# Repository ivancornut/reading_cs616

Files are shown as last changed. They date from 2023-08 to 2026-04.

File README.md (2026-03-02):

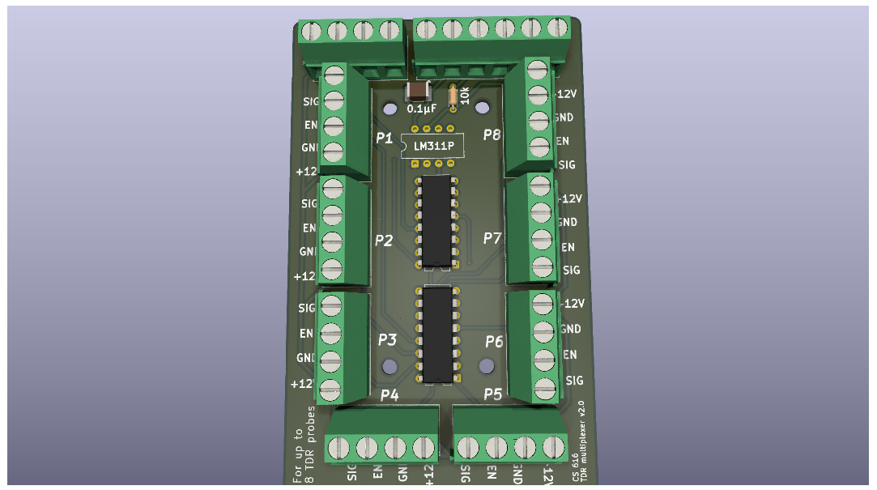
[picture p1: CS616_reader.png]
Multiplexer

# Reading CS616

The CS616 is a moisture sensor from Campbell. It measures the soil moisture using the TDR (Time domain relfectometry) technique. 
This is an efficient and accurate way to measure soil moisture. These sensors output a square wave with a period proportional to the soil moisture.
The output period is above 10 µS so readable by a Pi Pico. Unfortunately the output is a square wave from -0.7V to 0.7V which is not readable by the input pin of a 3.3V arduino micro-controller. 

The goal is to provide a way to read multiple CS616 sensors using a Pi Pico board. 

## Simple Schematic to read one sensor using a micro-controller
To convert the output of the sensor into something readable by a 3.3V µC we use a fast differential comparator, the LM311P. This idea was inspired by the design of a frequency counter found online [here](https://www.ee-diary.com/2022/07/high-frequency-counter-with-arduino.html#). Their design was adapted using an example circuit found in the datasheet of the comparator. 

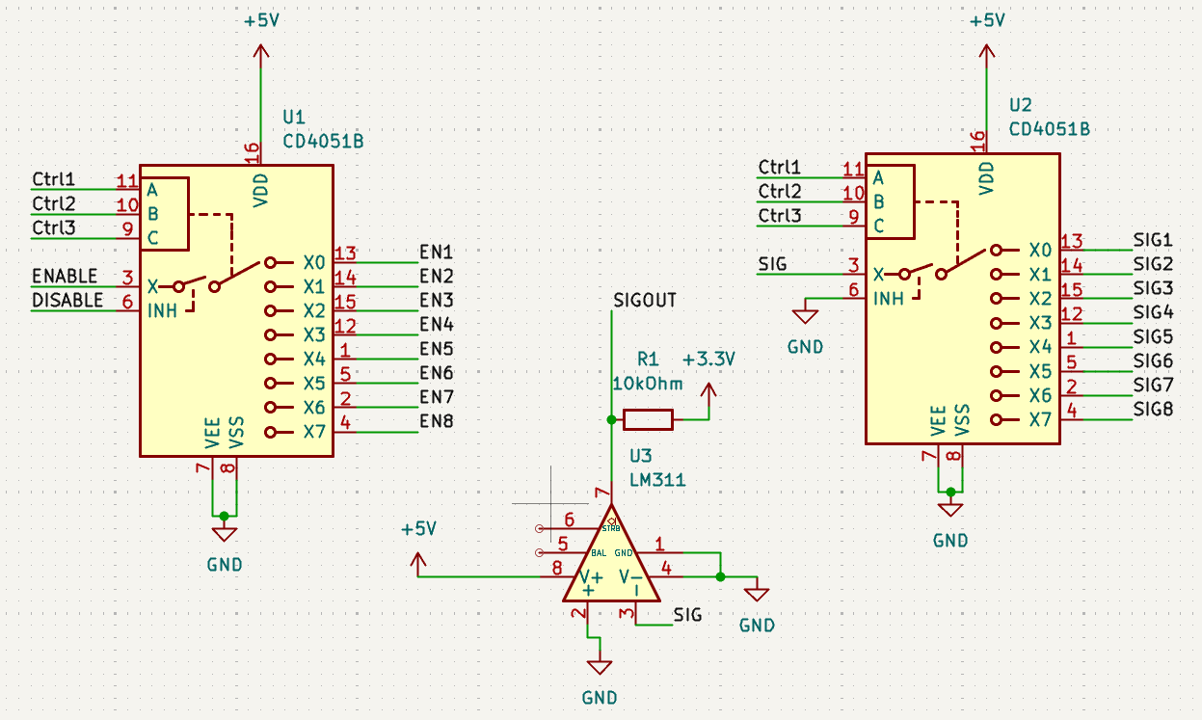
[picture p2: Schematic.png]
Comparator circuit


## Reading multiple CS616 sensors using one micro-controller
We combine the use of the comparator with the use of multiplexers that multiplex the enable and signal lines of the sensors.

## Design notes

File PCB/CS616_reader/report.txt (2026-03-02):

Info: Fini.
Info: Fini.
Tracé en '/home/cornut/Documents/dev_capteurs/reading_cs616/PCB/CS616_reader/Gerber_files/CS616_reader-F_Paste.gbr'.
Tracé en '/home/cornut/Documents/dev_capteurs/reading_cs616/PCB/CS616_reader/Gerber_files/CS616_reader-F_Paste.gbr'.
Tracé en '/home/cornut/Documents/dev_capteurs/reading_cs616/PCB/CS616_reader/Gerber_files/CS616_reader-B_Paste.gbr'.
Tracé en '/home/cornut/Documents/dev_capteurs/reading_cs616/PCB/CS616_reader/Gerber_files/CS616_reader-F_Silkscreen.gbr'.
Tracé en '/home/cornut/Documents/dev_capteurs/reading_cs616/PCB/CS616_reader/Gerber_files/CS616_reader-B_Silkscreen.gbr'.
Tracé en '/home/cornut/Documents/dev_capteurs/reading_cs616/PCB/CS616_reader/Gerber_files/CS616_reader-F_Mask.gbr'.
Tracé en '/home/cornut/Documents/dev_capteurs/reading_cs616/PCB/CS616_reader/Gerber_files/CS616_reader-B_Mask.gbr'.
Tracé en '/home/cornut/Documents/dev_capteurs/reading_cs616/PCB/CS616_reader/Gerber_files/CS616_reader-Edge_Cuts.gbr'.
Création du fichier Gerber "job" '/home/cornut/Documents/dev_capteurs/reading_cs616/PCB/CS616_reader/Gerber_files/CS616_reader-job.gbrjob'.
Tracé en '/home/cornut/Documents/dev_capteurs/reading_cs616/PCB/CS616_reader/Gerber_files/CS616_reader-B_Cu.gbr'.
Tracé en '/home/cornut/Documents/dev_capteurs/reading_cs616/PCB/CS616_reader/Gerber_files/CS616_reader-B_Cu.gbr'.
Tracé en '/home/cornut/Documents/dev_capteurs/reading_cs616/PCB/CS616_reader/Gerber_files/CS616_reader-B_Paste.gbr'.
Tracé en '/home/cornut/Documents/dev_capteurs/reading_cs616/PCB/CS616_reader/Gerber_files/CS616_reader-F_Silkscreen.gbr'.
Tracé en '/home/cornut/Documents/dev_capteurs/reading_cs616/PCB/CS616_reader/Gerber_files/CS616_reader-B_Silkscreen.gbr'.
Tracé en '/home/cornut/Documents/dev_capteurs/reading_cs616/PCB/CS616_reader/Gerber_files/CS616_reader-F_Mask.gbr'.
Tracé en '/home/cornut/Documents/dev_capteurs/reading_cs616/PCB/CS616_reader/Gerber_files/CS616_reader-B_Mask.gbr'.
Tracé en '/home/cornut/Documents/dev_capteurs/reading_cs616/PCB/CS616_reader/Gerber_files/CS616_reader-Edge_Cuts.gbr'.
Création du fichier Gerber "job" '/home/cornut/Documents/dev_capteurs/reading_cs616/PCB/CS616_reader/Gerber_files/CS616_reader-job.gbrjob'.
Tracé en '/home/cornut/Documents/dev_capteurs/reading_cs616/PCB/CS616_reader/Gerber_files/CS616_reader-F_Cu.gbr'.
Tracé en '/home/cornut/Documents/dev_capteurs/reading_cs616/PCB/CS616_reader/Gerber_files/CS616_reader-F_Cu.gbr'.
Attention: Correction de largeur. La valeur de correction doit être dans la plage  [0,000001 mm; 0,199999 mm]  pour les règles actuelles de conception.
Info: Fini.
Info: Fini.

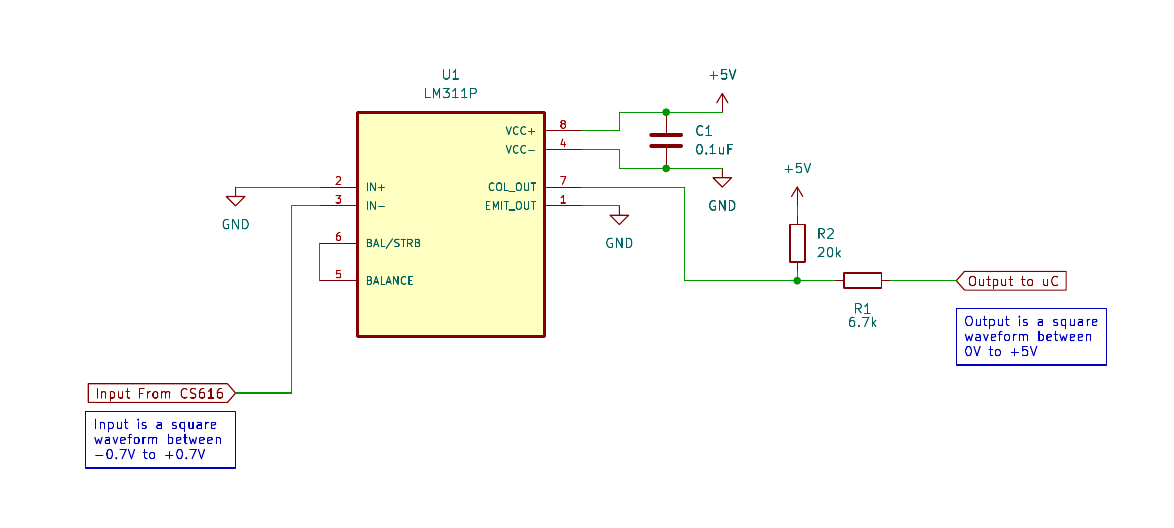
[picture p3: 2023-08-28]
Comparator_circuit.png

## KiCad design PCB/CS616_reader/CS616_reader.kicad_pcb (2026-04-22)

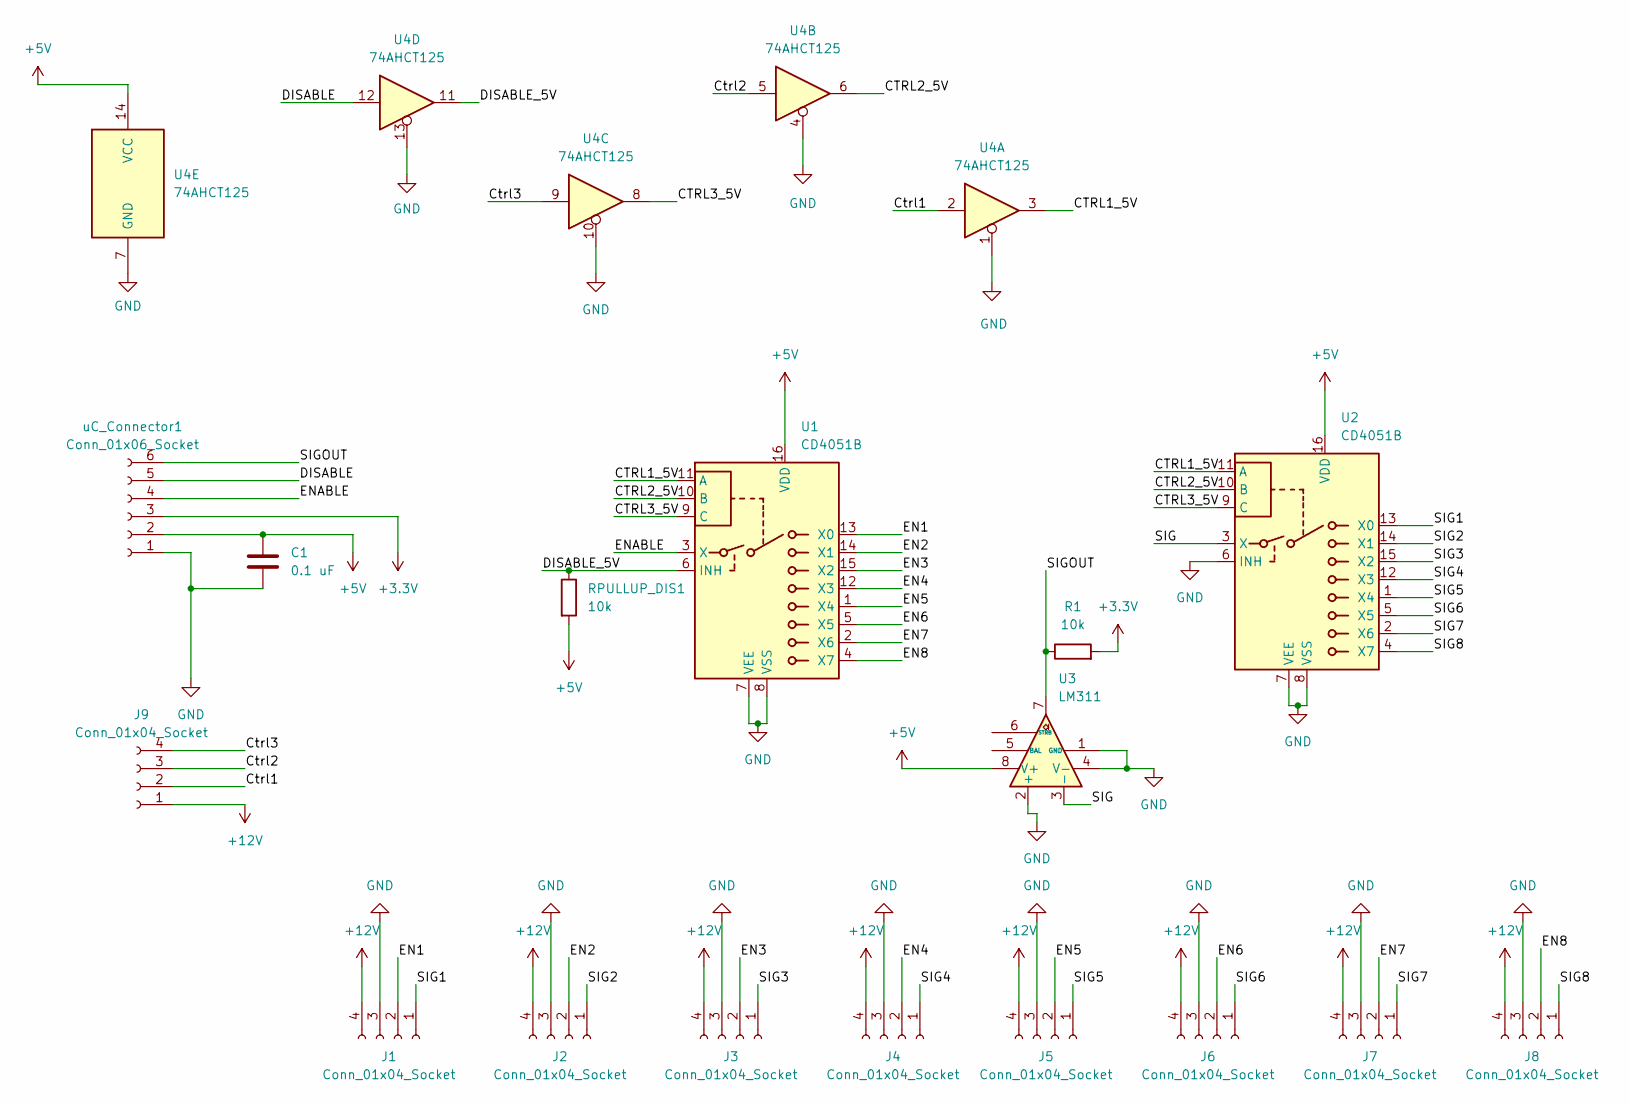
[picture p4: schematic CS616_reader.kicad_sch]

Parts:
C1: 0.1 uF; C_1812_4532Metric_Pad1.57x3.40mm_HandSolder
J1, J2, J3, J4, J5, J6, J7, J8, J9: Conn_01x04_Socket; TerminalBlock_Phoenix_MKDS-1,5-4-5.08_1x04_P5.08mm_Horizont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
R1: 10k; R_Axial_DIN0204_L3.6mm_D1.6mm_P5.08mm_Horizontal
RPULLUP_DIS1: 10k; R_Axial_DIN0204_L3.6mm_D1.6mm_P5.08mm_Horizontal
U1, U2: CD4051B; DIP-16_W7.62mm
U3: LM311; CERDIP-8_W7.62mm_SideBrazed
U4: 74AHCT125; DIP-14_W7.62mm
uC_Connector1: Conn_01x06_Socket; TerminalBlock_Phoenix_MKDS-1,5-6-5.08_1x06_P5.08mm_Horizont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

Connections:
+3.3V: R1.2, uC_Connector1.3
+5V: C1.1, RPULLUP_DIS1.2, U1.16 (VDD), U2.16 (VDD), U3.8 (V+), U4.14 (VCC), uC_Connector1.2; also elsewhere on the board
+12V: J1.4, J2.4, J3.4, J4.4, J5.4, J6.4, J7.4, J8.4, J9.1
/CTRL1_5V: U1.11 (A), U2.11 (A), U4.3
/CTRL2_5V: U1.10 (B), U2.10 (B), U4.6
/CTRL3_5V: U1.9 (C), U2.9 (C), U4.8
/Ctrl1: J9.2, U4.2
/Ctrl2: J9.3, U4.5
/Ctrl3: J9.4, U4.9
/DISABLE: U4.12, uC_Connector1.5
/DISABLE_5V: RPULLUP_DIS1.1, U1.6 (INH), U4.11; also elsewhere on the board
/EN1: J1.2, U1.13 (X0)
/EN2: J2.2, U1.14 (X1)
/EN3: J3.2, U1.15 (X2)
/EN4: J4.2, U1.12 (X3)
/EN5: J5.2, U1.1 (X4)
/EN6: J6.2, U1.5 (X5)
/EN7: J7.2, U1.2 (X6)
/EN8: J8.2, U1.4 (X7)
/ENABLE: U1.3 (X), uC_Connector1.4
/SIG: U2.3 (X), U3.3 (-)
/SIG1: J1.1, U2.13 (X0)
/SIG2: J2.1, U2.14 (X1)
/SIG3: J3.1, U2.15 (X2)
/SIG4: J4.1, U2.12 (X3)
/SIG5: J5.1, U2.1 (X4)
/SIG6: J6.1, U2.5 (X5)
/SIG7: J7.1, U2.2 (X6)
/SIG8: J8.1, U2.4 (X7)
/SIGOUT: R1.1, U3.7, uC_Connector1.6
GND: C1.2, J1.3, J2.3, J3.3, J4.3, J5.3, J6.3, J7.3, J8.3, U1.7 (VEE), U1.8 (VSS), U2.6 (INH), U2.7 (VEE), U2.8 (VSS), U3.1 (GND), U3.2 (+), U3.4 (V-), U4.1, U4.4, U4.7 (GND), U4.10, U4.13, uC_Connector1.1

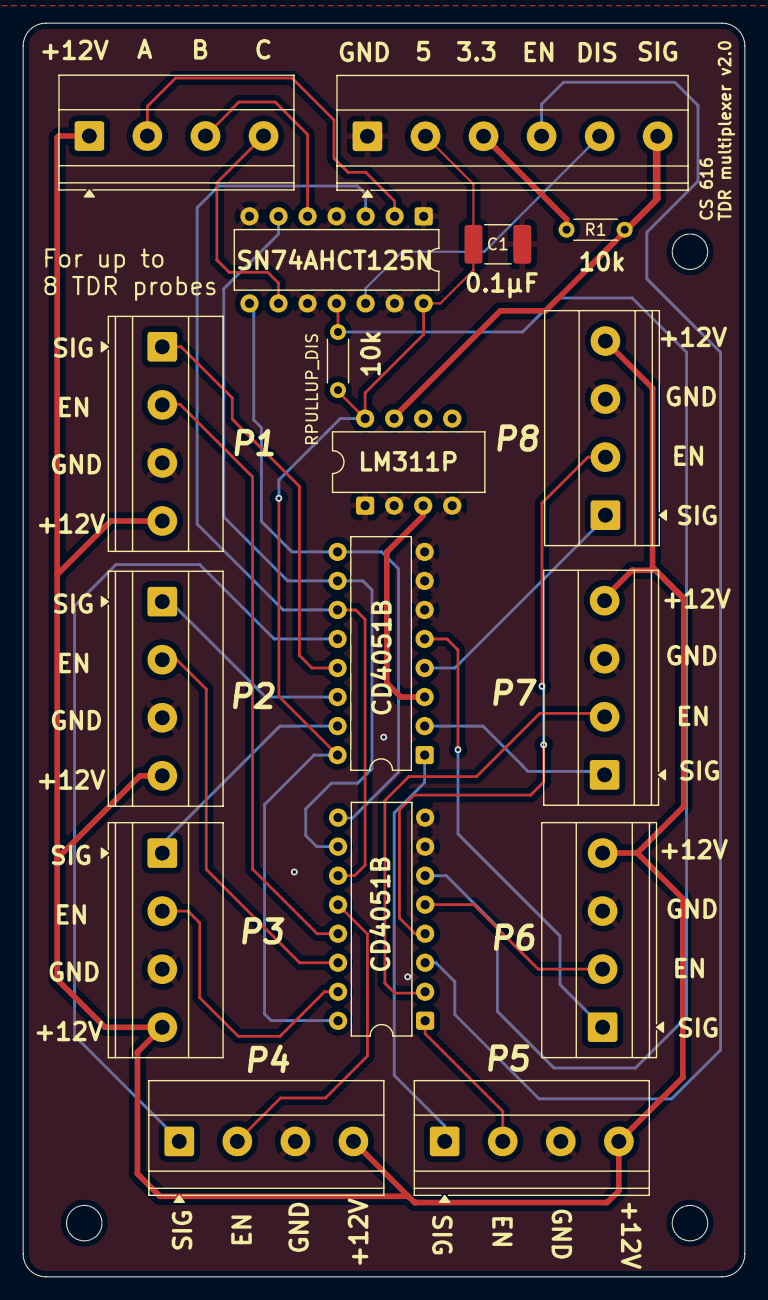
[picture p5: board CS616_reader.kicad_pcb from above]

Board: 2 copper layers, 63.2 x 109.7 mm, 17 parts (0 on the bottom side), 31 nets.

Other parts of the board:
RPULLUP_DIS: 10k; R_Axial_DIN0204_L3.6mm_D1.6mm_P5.08mm_Horizontal

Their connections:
+5V: RPULLUP_DIS.2; also elsewhere on the board
/DISABLE_5V: RPULLUP_DIS.1; also elsewhere on the board

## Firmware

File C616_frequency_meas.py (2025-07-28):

from counter import PWMCounter
from machine import Pin, PWM, Timer
from time import ticks_ms, ticks_diff, sleep, ticks_us

testing = False
testing_pin = 4 # GPIO address of testing pin
frequency_counting_pin = 7 # GPIO address of frequency counter

number_cs616 = 2 # number of CS616 attached to pico

enable_Pins_addr = [0,1,2,3,5,6,7,8,9,10,11,12] # the GPIO of pins for enabling CS616

if testing:
    # this is to test that the frequency counter pin is working
    # In this case connect the testing pin to the frequency counting pin
    pwm = PWM(Pin(testing_pin))
    pwm.duty_u16(1 << 15) # we shift 1 bit 15 which is equivalent to u16/2
    pwm.freq(39000)

enable_pins = []
period_sensor = []
VW_sensor = []

for i in range(0,number_cs616):
    try:
        enable_pins.append(Pin(enable_Pins_addr[i], Pin.OUT)) # create list with all pins as output
        enable_pins[i].value(0) # set all outputs to zero
    except:
        print("Issue setting Pin "+str(enable_Pins_addr[i]))
    period_sensor.append(9999)
    VW_sensor.append(9999)
        
def freq_measure(counter):
    sampling_time = 100000
    #global counter
    mean_freq = 0
    for i in range(1,11):
        counter.stop()
        counter.reset()
        cond = True
        last_check = ticks_us()
        counter.start()
        while cond:
            if ticks_diff(tmp := ticks_us(), last_check) >= sampling_time:
                freq = counter.read_and_reset() / (sampling_time / 1000000)
                mean_freq = mean_freq + (freq)/10
                cond = False
    if mean_freq == 0:
        print("error no frequency")
        print("---------------------------")
        period = 9999.9
        VW = 9999.9
    else:
        period = 1/mean_freq * 1000000 # in us
        VW=(-0.0663 + (-0.0063*period)+(0.0007*period**2))*100
        print(f"Frequency: {mean_freq:.2f}kHz")
        print(f"Period: {period:.2f}µs")
        print(f"Soil Moisture: {VW:.2f}%")
        print("---------------------------")
        #print(freq, period, VW)
    counter.stop()
    return period, VW

counter_freq = PWMCounter(frequency_counting_pin, PWMCounter.EDGE_RISING)
counter_freq.set_div() # Set divisor to 1 (just in case)
counter_freq.start() # Start counter

while True:
    print("yes")
    u = 0
    for i in enable_pins: # we iterate over all the CS616 sensors
        i.value(1)
        sleep(2+)
        try:
            period_sensor[u], VW_sensor[u] = freq_measure(counter_freq)
        except:
            #in case of issue
            period_sensor[u] = 9999.9 
            VW_sensor[u] = 9999.9
            print("Problem with frequency measurement")
        
        sleep(5)
        i.value(0)
        u = u+1
    sleep(1)

    

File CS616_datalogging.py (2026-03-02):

from counter import PWMCounter
from machine import Pin, PWM, Timer,I2C,lightsleep,WDT, idle, ADC
from time import ticks_ms, ticks_diff, sleep, ticks_us
import json
import urtc
import sdcard
import vfs
import os
import CD4051

class logger():
    ''' datalogger class that allows to save data
        should soon be in its own class and module '''
    
    def __init__(self,column_names = ["var1","var2","var3","var4"],rtc_clock=None):
        # initialising the SD card for the Pi Cowbell datalogger
        cs = Pin(17,Pin.OUT)
        spi = machine.SPI(0, baudrate=1000000,polarity=0,phase=0,bits=8,firstbit=machine.SPI.MSB,sck=Pin(18),mosi=Pin(19),miso=Pin(16))
        self.sd = sdcard.SDCard(spi, cs)
        self.filsys = vfs.VfsFat(self.sd)
        #vfs.mount(self.filsys, "/sd") # mount the SD card
        
        self.var_names = column_names # names of the columns in csv files
        self.rtc = rtc_clock
        
        self.battery_pin = ADC(28)
        self.voltage_drop_factor = 1/(21.47/(66.1+21.47))
        try:
            os.stat('info.json') # file exists and can be found
            with open('info.json','r') as f:
                config = json.load(f)
            self.file_prefix = config["device_name"]
            self.timestep = int(config["timestep"])
        except:
            self.file_prefix = "data"
        with open('logs.txt','a') as f:
            now = self.rtc.datetime() # check date
            f.write(f"restarted at {now.day,now.hour,now.minute}\n")
            
    def read_battery_voltage(self):
        sensor_value = 0
        for i in range(0,10):
            sensor_value = sensor_value + self.battery_pin.read_u16()/10
        self.battery_voltage = sensor_value * (3.3 / 65535) * self.voltage_drop_factor

    def agm_battery_soc(self):
        if self.battery_voltage >= 12.7:
            self.battery_SOC = 100.0
        elif self.battery_voltage >= 12.4:
            self.battery_SOC = 75 + 25 * (self.battery_voltage - 12.4) / 0.3
        elif self.battery_voltage >= 12.2:
            self.battery_SOC = 50 + 25 * (self.battery_voltage - 12.2) / 0.2
        elif self.battery_voltage >= 12.0:
            self.battery_SOC = 25 + 25 * (self.battery_voltage - 12.0) / 0.2
        elif self.battery_voltage >= 11.8:
            self.battery_SOC = 10 + 15 * (self.battery_voltage - 11.8) / 0.2
        else:
            self.battery_SOC = 0.0

    def save_data(self,data=[0,9,99,999]):
        vfs.mount(self.filsys, "/sd") # mount the SD card
        now = self.rtc.datetime() # check date
        # the device creates a new file every day this is easier to handle. 
        self.filename = "/sd/"+self.file_prefix+'_'+str(now.year)+"-"+str(now.month)+"-"+str(now.day)+".csv"
        # check if file exists and if doesn't create first line with column names
        try:
            os.stat(self.filename) # file exists and can be found
        except:
            with open(self.filename,'a') as f:
                # write the header
                f.write("DateTime,Battery_voltage,Battery_SOC")
                for name in self.var_names:
                    f.write(",")
                    f.write(name)
                f.write("\n")
        
        with open(self.filename,'a') as f:
            # write the data
            now = self.rtc.datetime()
            self.read_battery_voltage()
            self.agm_battery_soc()
            f.write(f"{now.year:04d}-{now.month:02d}-{now.day:02d}T{now.hour:02d}:{now.minute:02d}:{now.second:02d}")
            f.write(f",{self.battery_voltage:.3f},{self.battery_SOC:.3f}")
            for n,val in enumerate(data):
                f.write(",")
                f.write("%1.4f" % val)
            f.write("\n")
            print('Done with writing_to_file')
        vfs.umount("/sd") # unmount the SD card    
class datalogger_cs616:
    
    def __init__(self,meas_pin = 13,timestep=15,number_cs616=8,CS616=True,test=True): 
        #self.enable_Pins_addr = [6,7,8,9,10,11,12,13] # the GPIO of pins for enabling CS616
        self.timestep = timestep
        self.number = number_cs616
        self.proto = test
        
        self.enable_Pin = Pin(14,Pin.OUT) # Pin to enable sensors with 5V
        self.enable_Pin.value(0)
        
        self.enable_control = CD4051.CD4051(7,8,9) # control of the first CD4051 switch
        self.signal_control = CD4051.CD4051(10,11,12) # control of the second CD4051 switch
        
        if not self.proto:
            # intitialise i2C for urtc clock on Pi Cowbell datalogger shield
            self.i2c_clock = I2C(0,scl=Pin(5), sda=Pin(4))
            self.rtc = urtc.PCF8523(self.i2c_clock)
            
            # create the column names for each sensor
            col_names = []
            for i in range(0,number_cs616):
                col_names.append("TDR"+str(i)+"_us")
                col_names.append("TDR"+str(i)+"_WC%")
            self.Logging = logger(col_names,self.rtc)
            self.timestep = self.Logging.timestep
        
        # handle the frequency counting Pin 
        self.pin_counter = PWMCounter(meas_pin, PWMCounter.EDGE_RISING)
        self.pin_counter.set_div() # Set divisor to 1 (just in case)
        self.pin_counter.start() # Start counter
        self.pin_counter.stop() # Stop counter
        
        ''' Set up the watchdog, the max timeout on pi pico
        is 8333ms. The watchdog reinits the device if it
        is stuck. Very useful for dataloggers. This also
        means that we need to wake device from sleep'''
        self.watchdog = WDT(timeout=8000)
        
        self.led = Pin(25, Pin.OUT) # internal led of the Pi Pico
        self.led.value(0)
    
    def _hello(self):
        for i in range(0,10):
            self.led.value(1)
            sleep(0.3)
            self.watchdog.feed()
            self.led.value(0)
            sleep(0.5)
    
    def _cs616_measure(self):
        ''' The frequency measuring function
        the period of the CS616 is then used to deduce soil
        water content'''
        sampling_time = 100000
        mean_freq = 0
        for i in range(1,11):
            self.pin_counter.stop()
            self.pin_counter.reset()
            cond = True
            last_check = ticks_us()
            self.pin_counter.start()
            
            while cond:
                if ticks_diff(tmp := ticks_us(), last_check) >= sampling_time:
                    freq = self.pin_counter.read_and_reset() / (sampling_time / 1000000)
                    mean_freq = mean_freq + (freq)/10
                    cond = False
        try:
            period = 1/mean_freq * 1000000 # in us
        except:
            period = 9999
        print(period,mean_freq)
        return period
    
    def _convert_period_to_wc(self,period_value):
        # this function is given in the manual of the CS616
        VW=(-0.0663 + (-0.0063*period_value)+(0.0007*period_value**2))*100
        return VW
    
    def _meas_sequence(self):
        self.data_values = []
        
        for i in range(0,self.number):
            self.enable_control.set_output(i)
            self.signal_control.set_output(i)
            self.enable_Pin.value(1)
            sleep(0.5) # just wait for it to turn on
            if not self.proto:
                try:
                    value_1 = self._cs616_measure() # Measure frequency
                    value_2 = self._convert_period_to_wc(value_1) # convert freq to water content

                except:
                    value_1 = 999.9
                    value_2 = 999.9
            else:  
                try:
                    value_1 = self._cs616_measure() # Measure frequency
                    value_2 = self._convert_period_to_wc(value_1) # convert freq to water content
                    print("Values:",value_1, value_2)
                except:
                    value_1 = 999.9
                    value_2 = 999.9
            self.enable_Pin.value(0)
            self.data_values.append(value_1)
            self.data_values.append(value_2)
            self.watchdog.feed()
            self.led.value(1)
            sleep(0.1)
            self.led.value(0)
        self.enable_control.set_output(0) # puts all pins to 0
        self.signal_control.set_output(0) # puts all pins to 0
    
    def run(self):
        self._hello()
        while True:
            if self.proto:
                print("This is prototyping")
                self._meas_sequence()
                self.watchdog.feed()
                sleep(2)
            else:
                now = self.rtc.datetime()
                if (now.minute%self.timestep) == 0:
                    self._meas_sequence()
                    self.Logging.save_data(self.data_values)
                    print("Done saving data")
                    self.watchdog.feed()
                    for i in range(0,10):
                        self.enable_Pin.value(0)
                        lightsleep(5750)
                        self.watchdog.feed()
                        self.led.value(1)
                        sleep(0.05)
                        self.led.value(0)
                self.enable_Pin.value(0)
                lightsleep(5750)
                self.watchdog.feed()
                self.led.value(1)
                sleep(0.05)
                self.led.value(0)
            #idle()

sleep(5) # just some time so usb can connect before the program is launched
Datalogger = datalogger_cs616(meas_pin=13,timestep=2,number_cs616=8,CS616=True,test=False)
Datalogger.run()

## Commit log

2023-08-28 Creation of the repository
    [CS616.csv, CS616.kicad_pcb, CS616.kicad_sch]
2023-08-28 Addition of the simple comparator circuit
    [Simple_circuit.kicad_pcb, Simple_circuit.kicad_sch]
2025-08-05 Added comments and internal led blink for diagnostics
2025-08-06 Fixed mistake in signal select pin
2026-03-02 Improved PCB
    [CS616_reader-B_Cu.gbr, CS616_reader-B_Mask.gbr, CS616_reader-B_Paste.gbr, CS616_reader-B_Silkscreen.gbr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]
2026-03-02 addes small picture for pcb
    [CS616_reader.kicad_pcb]
2026-03-02 Cleaned the repository
    [CS616.csv, CS616.kicad_pcb, CS616.kicad_sch, Simple_circuit.kicad_pcb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]
2026-04-22 Added logic level converter to pcb
    [CS616_reader.kicad_pcb, CS616_reader.kicad_sch]
2026-04-22 Improvements to pcb
    [CS616_reader.kicad_pcb]
